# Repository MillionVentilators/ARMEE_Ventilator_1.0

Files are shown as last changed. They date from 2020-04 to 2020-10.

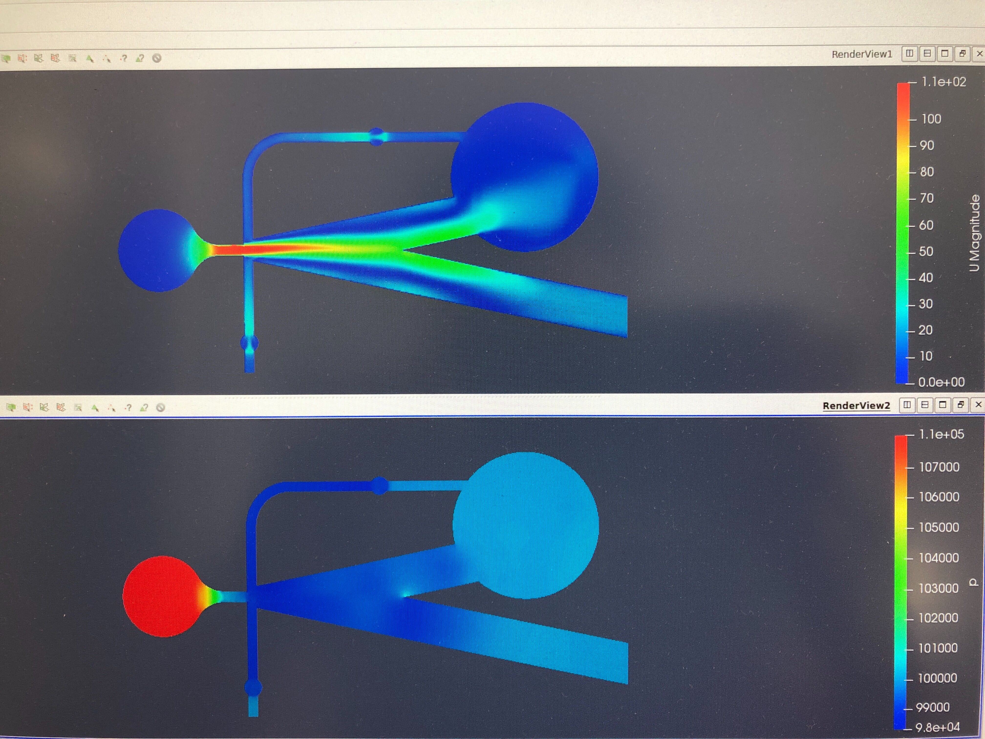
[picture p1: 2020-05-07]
experimental/Monostable/images/Image from iOS (16).jpg

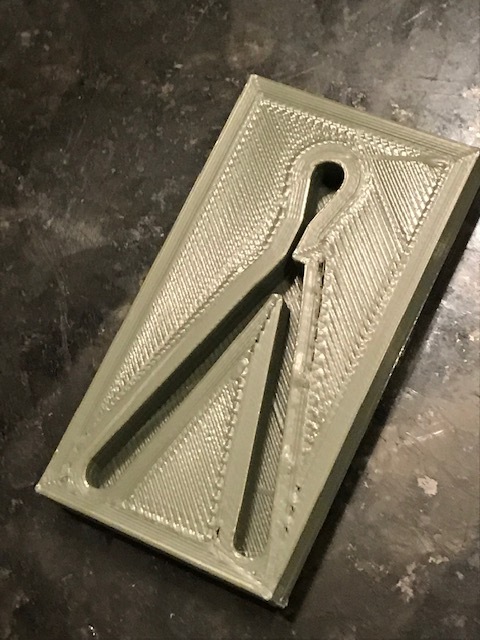
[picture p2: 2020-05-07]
experimental/Monostable/images/IMG_2069.jpg

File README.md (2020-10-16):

# ARMEE Ventilator

Automatic Respiration Management Exclusively for Emergencies

www.ARMEEVentilator.com (previously www.ARMEEVent.com)

Email: ArmyVent@gmail.com

Introduction: (click for video)
ARMEE Ventilator Introduction (https://www.youtube.com/watch?v=14Afl-Eg2tM "ARMEE Ventilator Introduction")

## INTRO

This repository contains plans for a device which controls air (or gas) flow so that its output alternates between two pressure levels.  The pressures, flow rates and cycle times are similar to the typical output of a mechanical ventilator.  *It has no moving parts*, and could be produced very rapidly, at low cost and in very large numbers if needed.

The original design dates to the early 1960s:
* J.W. Joyce, Jr. ["TM 68-30 The Army Emergency Respirator"](./research/1968_Army_Emergency_Respirator.pdf). Harry Diamond Labs, US Army Materiel Command, 1968

We are working to modify it to make the output better match modern requirements.

This is an open source hardware project: all work is licensed under the CERN Open Hardware Licence v2 (strongly reciprocal).

## HOW TO CONTRIBUTE

Get the necessary [Equipment](./documentation/Equipment.md): a source of compressed air, pressure and flow gauges and a test lung.

Build one of the [Stable Models](./stable/), following the [Build Instructions](./documentation/Build_Instructions.md): the recommended method is to use a CNC mill to make this out of plastic, but feel free to experiment.

The [Monostable](./experimental/Monostable) design is currently the most promising model, with results close to target parameters and very stable switching.  Check it out.

Run some tests following the [Test Instructions](./documentation/Test_Instructions.md).

Try to modify the design so as to address some of the [Open Issues](./documentation/Open_Issues.md).

Participate in the discussion on [Helpful Engineering](http://helpfulengineering.slack.com) at #project-oscillating-ventilator or our [Slack](http://millionvents.slack.com).

## MORE DOCUMENTATION

(Now somewhat outdated) documentation: 
- https://docs.google.com/document/d/1ZnPGnA-GKtFLsJEDVVLLKqNAKSk3q6F47YqvtuoJVXw/

## DISCLAIMER

This is not a medical device, and is not intended to be used as part of a medical device. It is especially not intended to be used in critical life support equipment. It comes with ABSOLUTELY NO WARRANTY. If you build it and use it, you do so at your own risk. If you build devices incorporating this design and use them for any application, it is up to you to verify the performance is suitable for your application and complies with all applicable laws.

## COPYRIGHT AND LICENSE

Copyright 2020 
- Ryan Whitney M.ryan.whitney@gmail.com (PEEP Loop Models)
- Alex Izvorski aizvorski@gmail.com (Original Dimensions/Models)
- Chris Jung Chris@braeburnacoustics.com (CNC Machining Models)
- Arrtemio Mendoza artexmg@gmail.com (3D Printing Models)

This Source (CAD files and other design materials) describes Open Hardware and is licensed under the CERN-OHL-S v2.

You may redistribute and modify this Source and make products using it under the terms of the CERN-OHL-S v2 (https:/cern.ch/cern-ohl).

This documentation is distributed WITHOUT ANY EXPRESS OR IMPLIED WARRANTY, INCLUDING OF MERCHANTABILITY, SATISFACTORY QUALITY AND FITNESS FOR A PARTICULAR PURPOSE. Please see the CERN-OHL-S v2 for applicable conditions.

Source Location: https://github.com/MillionVentilators/ARMEE_Ventilator_1.0

As per CERN-OHL-S v2 section 4, should You produce hardware based on this Source, You must maintain the Source Location visible on the external case of the hardware or other product you make using this Source.

## DISCLAIMER OF WARRANTY, EXCLUSION AND LIMITATION OF LIABILITY

Additionally, the following important disclaimers from the CERN-OHL-S v2 license apply to all use (reproduced below for clarity). Do not download or use these files unless you have read and agree with the following.

6.1 DISCLAIMER OF WARRANTY -- The Covered Source and any Products are provided 'as is' and any express or implied warranties, including, but not limited to, implied warranties of merchantability, of satisfactory quality, non-infringement of third party rights, and fitness for a particular purpose or use are disclaimed in respect of any Source or Product to the maximum extent permitted by law. The Licensor makes no representation that any Source or Product does not or will not infringe any patent, copyright, trade secret or other proprietary right. The entire risk as to the use, quality, and performance of any Source or Product shall be with You and not the Licensor. This disclaimer of warranty is an essential part of this Licence and a condition for the grant of any rights granted under this Licence.

6.2 EXCLUSION AND LIMITATION OF LIABILITY -- The Licensor shall, to the maximum extent permitted by law, have no liability for direct, indirect, special, incidental, consequential, exemplary, punitive or other damages of any character including, without limitation, procurement of substitute goods or services, loss of use, data or profits, or business interruption, however caused and on any theory of contract, warranty, tort (including negligence), product liability or otherwise, arising in any way in relation to the Covered Source, modified Covered Source and/or the Making or Conveyance of a Product, even if advised of the possibility of such damages, and You shall hold the Licensor(s) free and harmless from any liability, costs, damages, fees and expenses, including claims by third parties, in relation to such use.

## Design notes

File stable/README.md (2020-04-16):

# Models

## Harry_Diamond_Respirator

(step and f3d files)

A replica of the original 1960s vintage US Army device.

Modeler: Alex Izvorski

Dimensions were obtained from a physical museum piece found in an art gallery in Chicago which is one of the only known copies in existence (so far) of the original 1968 US ["Army Emergency Respirator"](./research/1968_Army_Emergency_Respirator.pdf) developed at Harry Diamond Labs.

If constructed carefully, this is expected perform identically to the original, cycling at a useful range of pressures/rates depending on input flow and calibration; and also including having a negative end pressure (which is not a desirable property).  

Note: we have had problems with reproducibility, probably because of small air leaks between the two halves of the device.  Dimensions and surface finish are also very important, probably +-0.02mm and ISO N6 finish or better.

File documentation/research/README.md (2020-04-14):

# References

Repository to host non-copyrighted patents and research materials found through our development process, as well as link references to online copyrighted versions.

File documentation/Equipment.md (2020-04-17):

# Equipment

## Compressed air

A source of pressurized air capable of 100 lpm (2 cfm) at 340 kPa (50 psi)

Suggested: small oil-free air compressor, eg Porter Cable C2002

Set the output of the compressor to a regulated 50psi, and connect a precision flow adjustment valve: McMaster-Carr 46425K12 or equivalent.

## Medical gas flow analyzer or ventilator tester

Device intended for certifying performance of ventilators in hospitals; contains pressure, flow and gas composition sensors.

Suggested 1: Fluke VT Plus HF; Fluke VT650 or VT900; TSI Certifier 4080; IMT Citrex H3, H4, H5.
These are expensive, typically > $2000 used.

Suggested 2: Siargo FS6122 or certain Sensirion  / Honeywell sensors have the right specs, but are not easy to interface

If gas flow analyzer is unavailable, a pressure gauge and flow gauge may be used as a substitute in a pinch.

## Pressure gauge

Pressure gauge capable of measuring 0-50 cmH2O with <1 cmH2O accuracy

Suggested 1: HT Instrument HT 805 Bluetooth Digital Manometer

Suggested 2: U tube manometer made out of 50-80 cm long piece of clear tubing with 1/4" or 1/8" inner diameter (eg aquarium PVC tubing)

Note: these pressures are far too low for most pressure gauges, other than the gauges used for HVAC service.

## Flow gauge

Flow gauge capable of measuring +-50 lpm air flow with <1 lpm accuracy.  (+-100lpm and <0.1 lpm accuracy is preferred) 

Suggested 1: medical flow meter (combination rotameter and needle valve) eg Timeter, Amvex, Ohmeda brand - this is not ideal, but don't really have a recommendation for a good digital sensor yet.  Most of these only span 0-15 lpm; may need more than one to cover 0-15 and 0-50 ranges.

Suggested 2: use a known resistance (~5mm hole in much larger tube) and differential pressure gauge from above to convert pressure drop to flow - also not ideal, have to always do math to convert, flow is proportional to square root of pressure drop.

## Test lung

A lung simulator with known (and preferably adjustable) resistance and compliance, within the range of C20-C50 ml/cmH2O and R5-R20 cmH2O/(liter/second).

Suggested: rigid vessel 30-70 liters (7.5-19 gallons) in size, with an entry opening restricted to 5-8mm in diameter.  Follow directions in this article [How To Make Your Own Accurate Test Lungs](https://medium.com/@RobertLeeRead/how-to-make-your-own-accurate-test-lungs-for-testing-emergency-ventilators-2d68fe5ac460)

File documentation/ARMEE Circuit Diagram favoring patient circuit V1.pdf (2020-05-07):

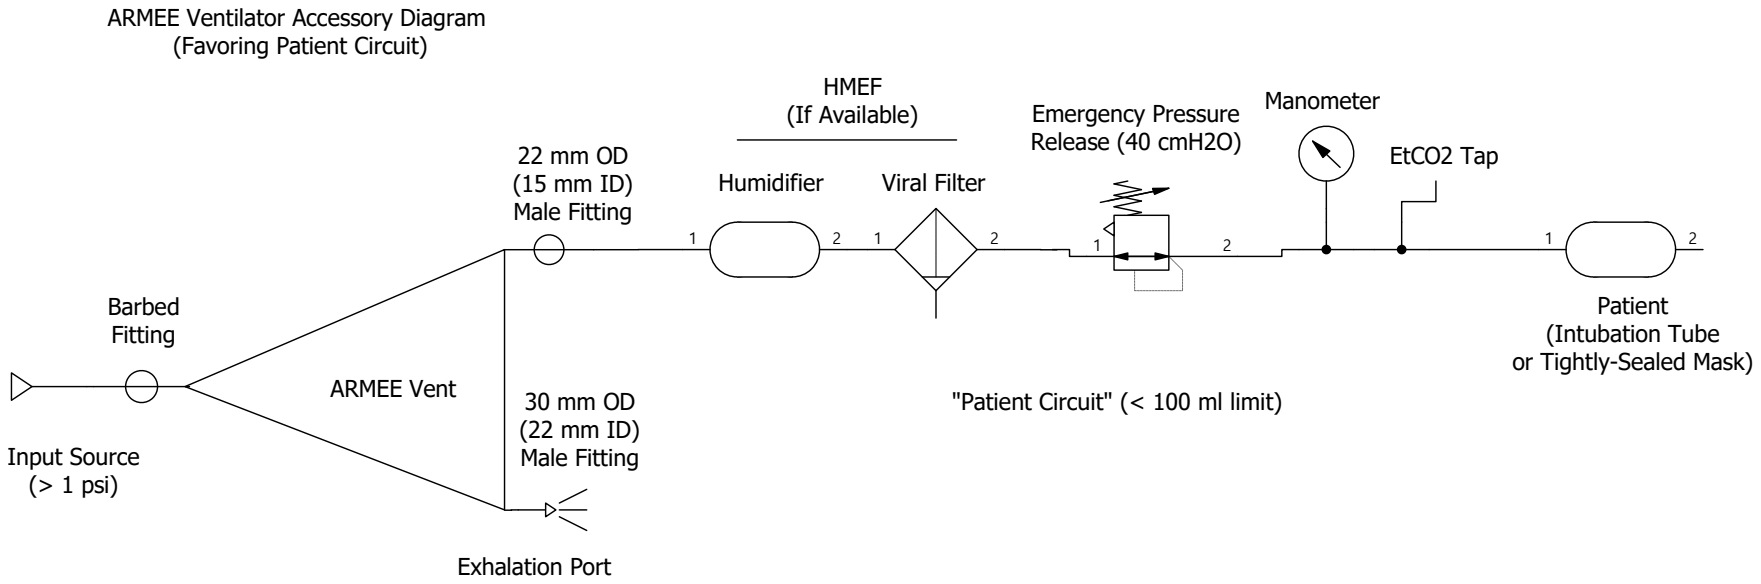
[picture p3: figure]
EtCO2 Tap; Manometer; Patient (Intubation Tube or Tightly-Sealed Mask); Emergency Pressure Release (40 cmH2O); Input Source (> 1 psi); ARMEE Ventilator Accessory Diagram (Favoring Patient Circuit); Viral Filter; HMEF (If Available); Exhalation Port; 22 mm OD (15 mm ID) Male Fitting; Barbed Fitting; Humidifier; 30 mm OD (22 mm ID) Male Fitting

"Patient Circuit" (< 100 ml limit) ARMEE Vent

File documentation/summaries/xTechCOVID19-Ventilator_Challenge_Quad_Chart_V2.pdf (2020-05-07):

## Interstate Disaster Medical Cooperative

## Automatic Respiration Management Exclusively for Emergencies

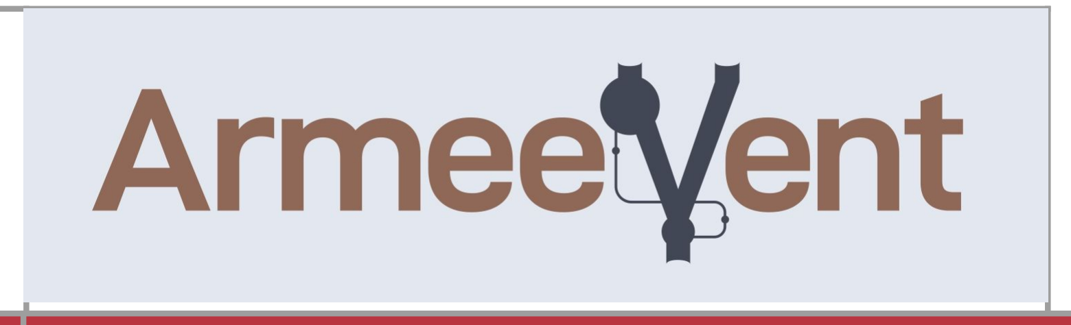
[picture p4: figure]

Tech. & Team | Mission Alignment | Technical Viability

Resubmission:

ARMEE Vent
Inspired by 1960s
designs and modified for
positive PEEP

Device Diagram:

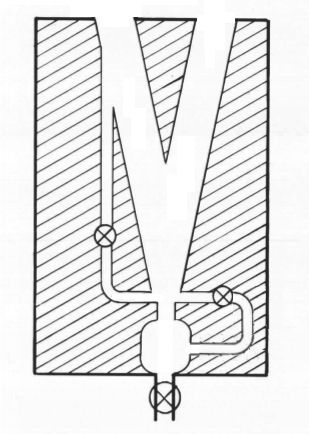
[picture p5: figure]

Core Team:
EMS Medical Director,
Medical Device Engineer,
Manufacturing Expert,
CFD Scientist,
Project Manager

Device is rugged, solid-state, has no moving parts, and is roughly the size/weight of a deck of cards - making it suitable for any kit. It is pneumatic (air-powered) and runs on low-pressure air or O2. This is a Pressure-Controlled device which also allows patient-triggered breathing, suitable for invasive or non-invasive ventilation. It can be customized to target any of the following: positive PEEP (5-20), PIP (15-35), I:E ratio (1:1 to 1:3), RR (0-60), TV (50-1000), for large or small patients with healthy lungs or damaged ones. The device is modular, fitting standard hospital tubing, and can operate standalone or with a suite of alarms/sensors/emergency valves, optionally included.

We use well-researched fluid dynamics science (fluid amplifiers) to build a suite of devices with pressure profiles built-in to the geometry of the devices to offer a range of PIP/PEEP/I:E ratio combos which can be targeted for different patient sizes and lung-health levels. While an unusual way to solve the problem, patients infrequently have their prescriptions changed in an emergency/pandemic situation, so simply swapping device models to match at those times is sufficient - and we offer the ability for more fine-grained adjustments via changing Input Flow as well. Multiple doctors endorse this approach already, and will be given rigorous data charts to guide applicability of the device.

Regulatory | Speed

Originally based on 1965 US Army ventilator research,
which was tested on dogs and humans successfully, we
have modified the designs and are underway with our own clinical testing. The design is very simple, easily cleaned or disposed-of, and runs indefinitely given a consistent flow of air. It can be easily swapped for a BVM, or fitted with (optional) additional safety precautions which give it full alarm and sensor functionality. Aside from an input flow rate of 20-30 lpm (which version 2 will fix), the device meets the UK's RMVS ventilator standards, and we expect it to pass EUA regulations once the final product is packaged.

A single CNC machine could immediately begin producing hundreds of units per day at sub-$30 ppu. Injection Molding: thousands per day, sub-$5. 3D printing: around 10 per day, sub-$5 ppu - useful for forward-deployment or on-demand production. Overall: 10k could be made in one day with 20-30 CNC machines with no lead-in time. That said, we recommend a sub-5-minute quality test per device, and we warn that the optional alarms/sensors may not match production speed. These are easier to source or create out of existing materials though, and may not be needed for every patient. We have several interested manufacturing partners.

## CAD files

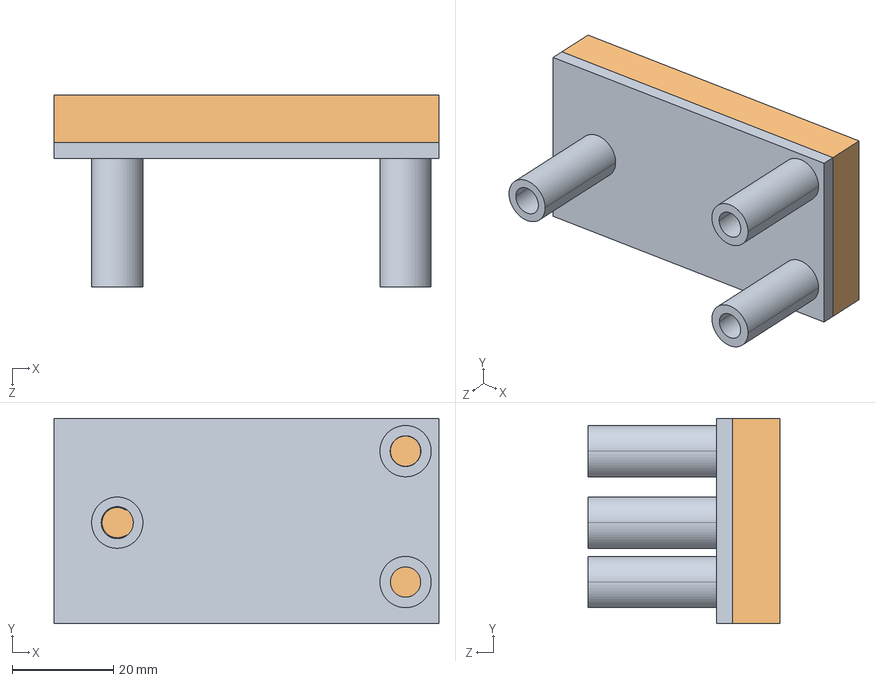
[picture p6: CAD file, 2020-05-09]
experimental/Monostable/Assembly_Monostable Fluidic Amplifier_Alpha Design_Nozzle_1.3mm__Radius_63.5mm__Channel Depth_6mm__Fillet_0mm.STEP
76.2 x 40.6 x 38.0 mm

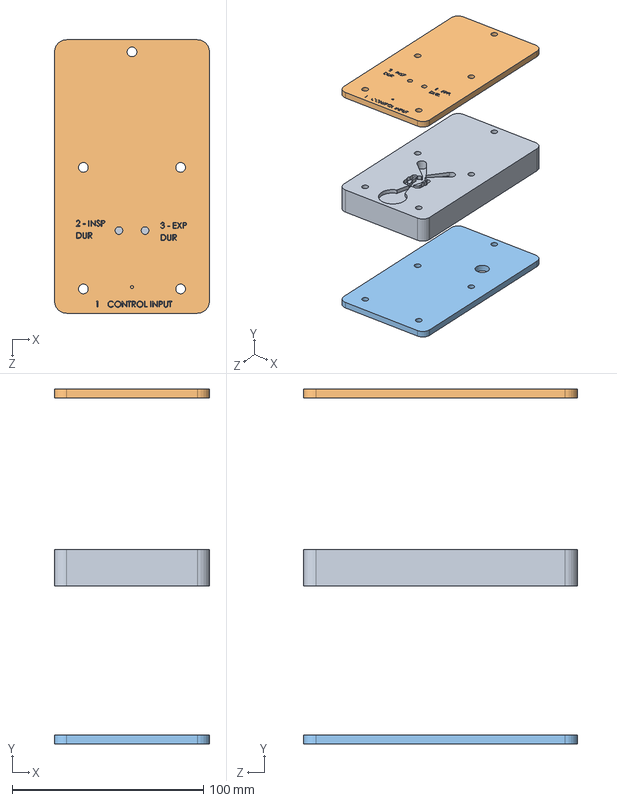
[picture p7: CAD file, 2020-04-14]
experimental/misc/Volume_Control/models/v2_whitney/NASA Army Vent Assm 02.SLDASM
81.0 x 185.4 x 142.9 mm
NASA Army Vent Body 02
Nasa Vent Plate 02, Control Side
Nasa Vent Plate 02, Flow Side

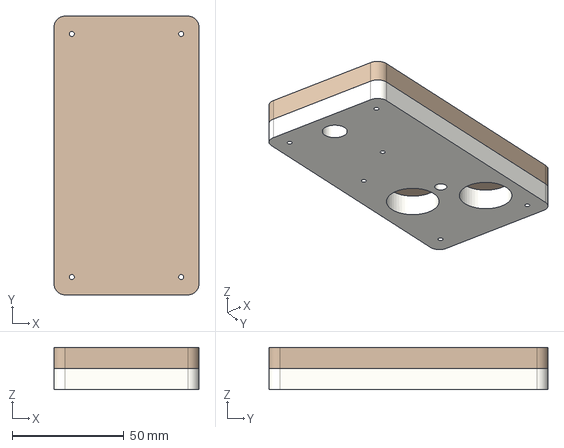
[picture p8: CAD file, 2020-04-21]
experimental/Exhaust_PEEP/Exhaust_PEEP v7.step
65.0 x 125.0 x 19.1 mm

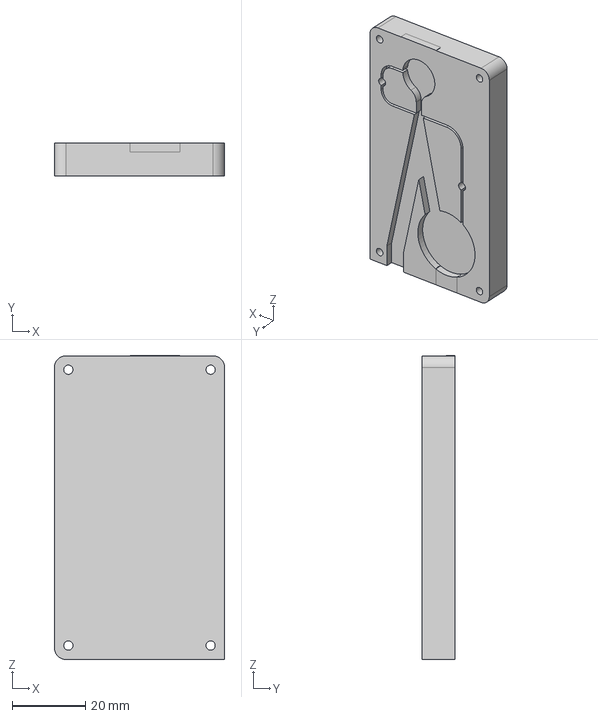
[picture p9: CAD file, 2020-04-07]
experimental/Loop_PEEP/models/CNC_machining/ARMEE_1.0_machinable.step
46.5 x 8.89 x 83.1 mm

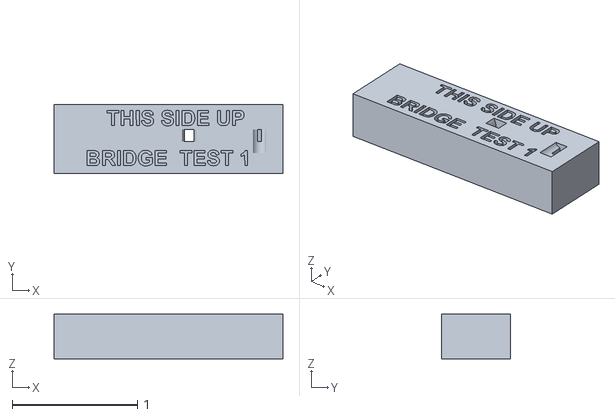
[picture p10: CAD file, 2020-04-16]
experimental/Loop_PEEP/models/FDM_3D_Printed_Brick/Bridge Test 1.stl
1.83 x 0.55 x 0.356

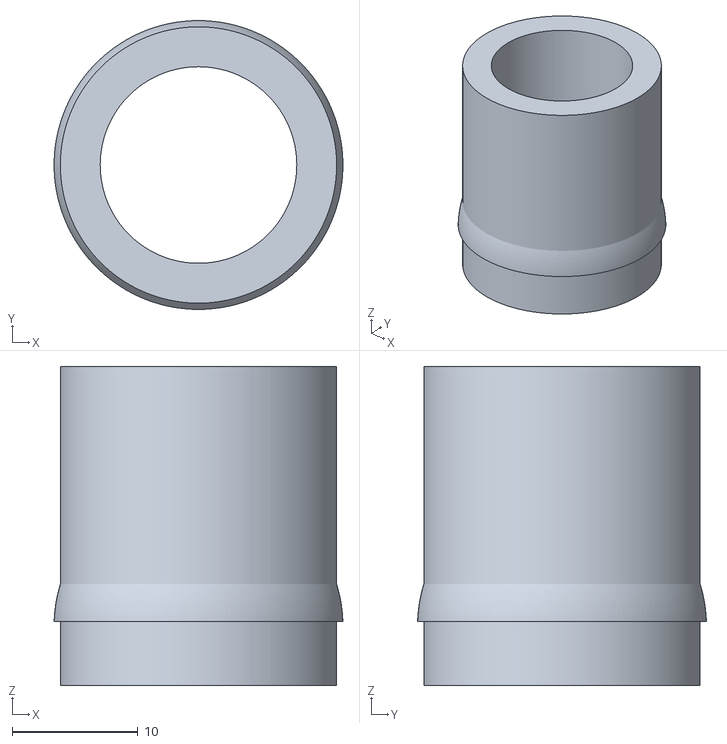
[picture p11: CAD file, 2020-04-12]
experimental/Loop_PEEP/models/FDM_3D_Printed_Snap/Outlet Armee1.stl
23.0 x 23.0 x 25.4

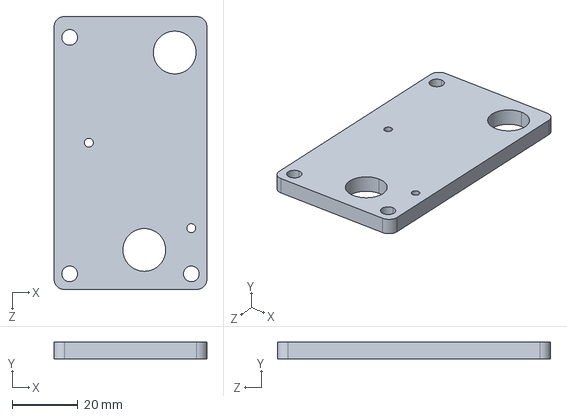
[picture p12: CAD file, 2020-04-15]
experimental/Loop_PEEP/models/HPDC_estimates/Army Vent PEEP 02, Lid_HPDC_r0.STEP
46.5 x 5.16 x 83.0 mm

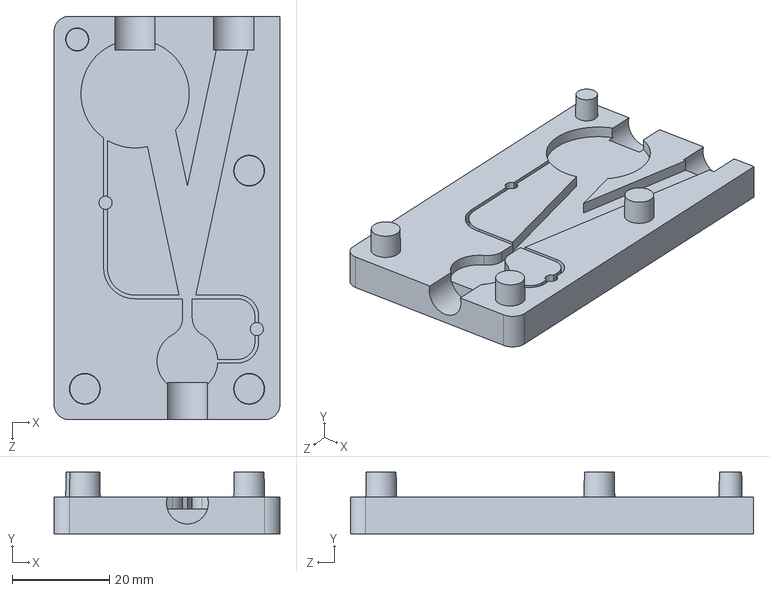
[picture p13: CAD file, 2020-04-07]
experimental/Loop_PEEP/models/reference_design/v2_whitney/ARMEE_1.0_base.sldprt
46.5 x 12.7 x 83.0 mm

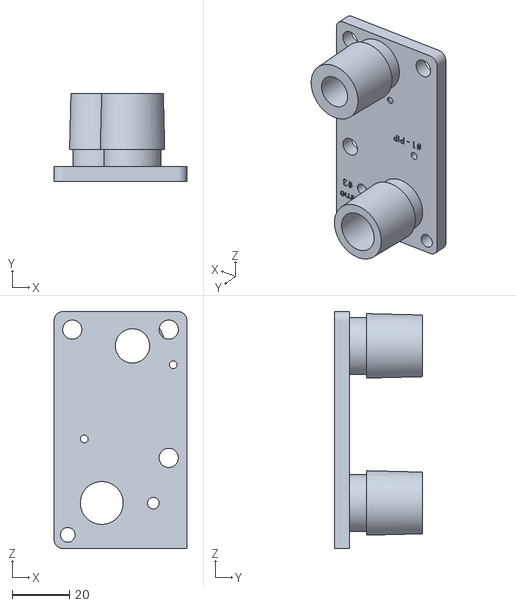
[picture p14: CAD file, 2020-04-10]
experimental/Loop_PEEP/models/reference_design/v3_whitney/Army Vent PEEP 03, Lid_20200410.STL
46.5 x 30.7 x 83.0

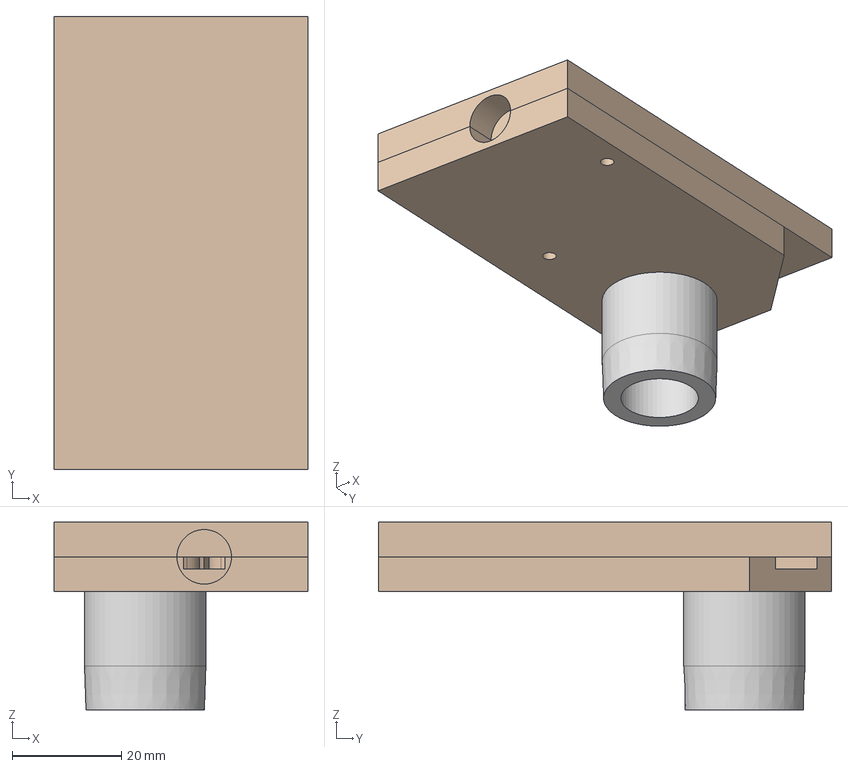
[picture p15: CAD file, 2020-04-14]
experimental/Loop_PEEP/models/reference_design/v4_whitney/Harry_Diamond_PEEP_Ryan v4.step
46.5 x 83.0 x 34.4 mm

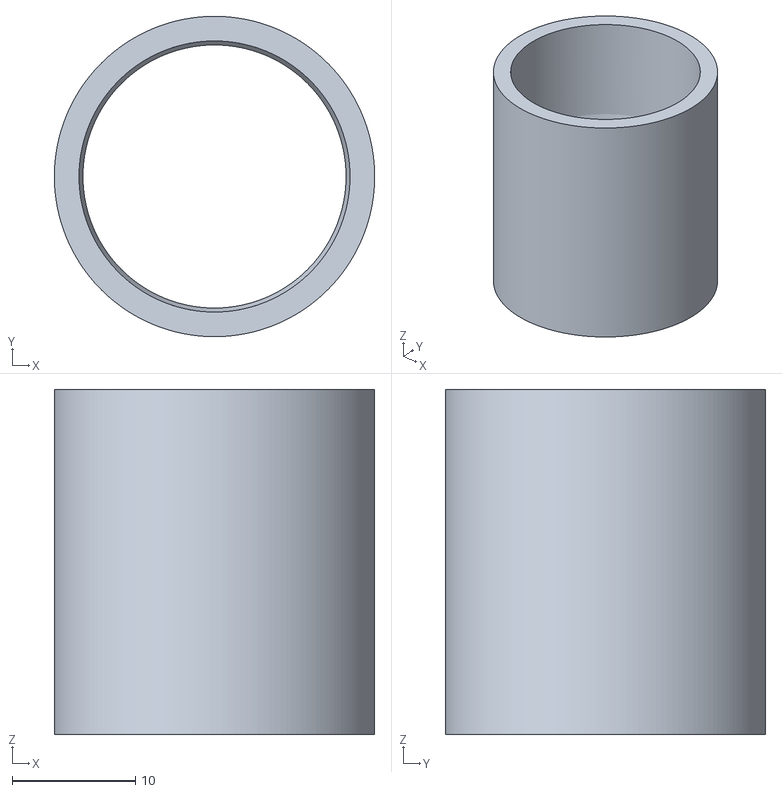
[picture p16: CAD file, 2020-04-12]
experimental/misc/Fittings/Couple 22mm Male.stl
26.0 x 26.0 x 28.0

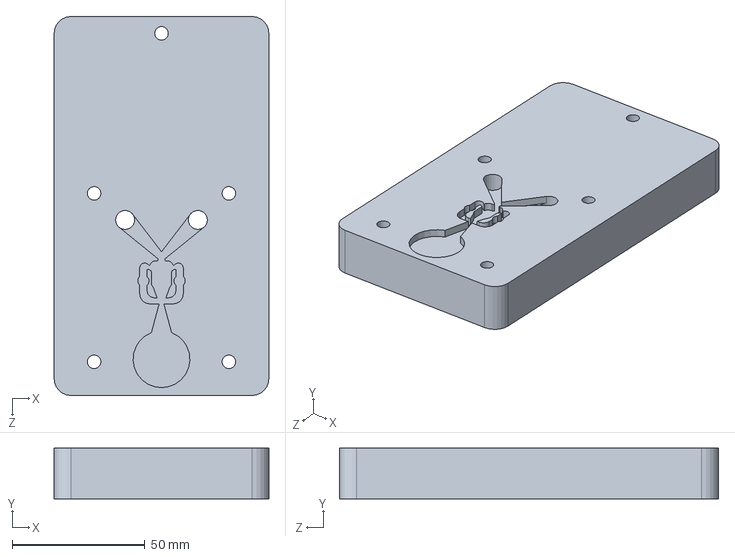
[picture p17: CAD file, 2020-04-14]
experimental/misc/Volume_Control/models/v2_whitney/NASA Army Vent Body 02.SLDPRT
81.0 x 19.1 x 142.9 mm

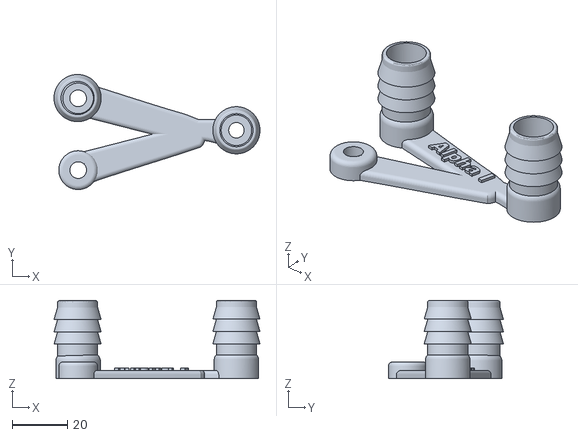
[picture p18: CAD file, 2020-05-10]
experimental/Monostable/Highly Printable - Alpha I/FDM/Two Parts/Alpha I Rev1 - Top.stl
74.3 x 41.5 x 28.2

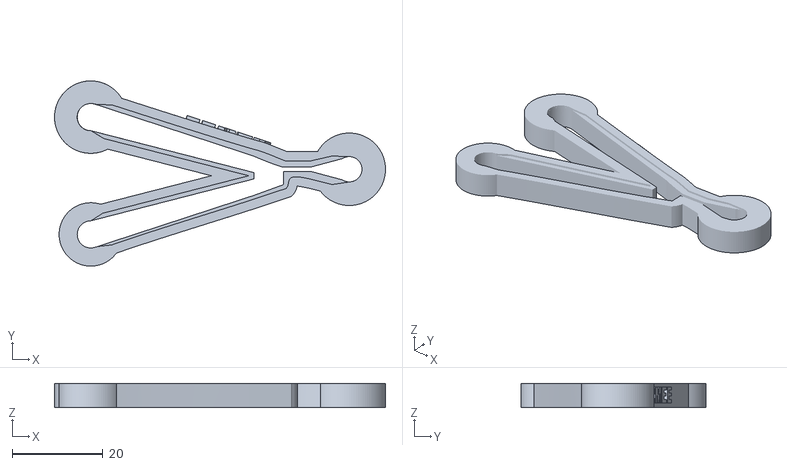
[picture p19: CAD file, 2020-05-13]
experimental/Monostable/Highly Printable - Alpha I/FDM/Unibody/Alpha I Rev1 - Testing Gasket.stl
73.1 x 40.9 x 5.31

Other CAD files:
experimental/Harry_Diamond_DFM/Harry_Diamond_DFM v4.step
experimental/Loop_PEEP/models/reference_design/v5_whitney/Harry_Diamond_PEEP_Ryan v5.step
experimental/Loop_PEEP_3Way/Loop_PEEP_3Way v3.step
experimental/Monostable/Highly Printable - Alpha I/SLA/Alpha I Rev1 - Unibody SLA.stl
experimental/Exhaust_PEEP/Exhaust_PEEP v7.f3d
experimental/Harry_Diamond_DFM/Harry_Diamond_DFM v4.f3d
experimental/Loop_PEEP/models/CNC_machining/ARMEE_1.0_machinable.f3d
experimental/Loop_PEEP/models/CNC_machining/ARMEE_1.0_test_rig.f3d
experimental/Loop_PEEP/models/CNC_machining/ARMEE_1.0_test_rig.step
experimental/Loop_PEEP/models/FDM_3D_Printed_Brick/ARMEE_1.0_printable_brick_fat_feedback.stl
experimental/Loop_PEEP/models/FDM_3D_Printed_Brick/Armee1 - Unibody Brick V1.1.stl
experimental/Loop_PEEP/models/FDM_3D_Printed_Brick/ArmyVentPEEP02 BRICK REV AMG.stl
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

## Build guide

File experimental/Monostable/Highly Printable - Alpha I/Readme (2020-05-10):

READ THIS BEFORE ANYTHING, you will need it!
Prepared by Artemio Mendoza

Before we start, let me say that THIS VENTILATOR IS NOT A MEDICAL EQUIPMENT, it is NOT INTENTED TO BE USED IN HUMAN PATIENTS.

This is a single piece ventilator (unibody). It is highly printable using either FDM or SLA 3D printers.

SLA.

For SLA it is as simple as printing in one single piece. Nothing much to add here, just get the STL from SLA directory and print it.
Of course you need to orient the print to avoid suction due to cups formation by the internal channels of the print. 
But you already know that, after all you have a SLA printer! :-) 

FDM.

1- Unibody version:

In order to print a single body ventilator using a FDM I developed a technique I call assisted bridging (or eZ-bridging or patching). 
It consists in pre-printing a flat support to be placed manually latter in the print to scaffold the next layer. 
Such a layer will become the ceiling of the print.

In order to place the printed support (or patch) you will need to stop the print, place the patch manually and then 
continue printing from where it stopped. This can be achieved modifying the Gcode either manually or by script 
in your slicing software. You would find the document "eZ-bridging.doc" usefull to get more details on this technique.

It is simpler than you think and once you get the hang of it, you will be able to bridge other pieces you always wanted to print, 
but you cannot because your printer did not like bridging. Now she will like bridging.

2.- Two parts version:

If for some reason you want to print the ventilator in two parts, you can find this two pieces in the directory "Two Parts". 
You can print both pieces and then glue them together. 

Final words: THIS VENTILATOR IS NOT A MEDICAL EQUIPMENT, it is NOT INTENTED TO BE USED IN HUMAN PATIENTS!

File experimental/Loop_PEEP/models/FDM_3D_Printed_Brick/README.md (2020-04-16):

# 3D-Printed "Brick" Version

by Artemio Mendoza

A single-print "brick" version made for FDM 3D Printers

1) Look the picture "how to orient the piece for printing"

2) Print the test pieces to validate your printer capabilities

Good luck!

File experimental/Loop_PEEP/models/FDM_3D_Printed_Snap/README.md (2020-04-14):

# 3D-Printed "Snap" Version

by Artemio Mendoza

A single-print "snap" version made for FDM 3D Printers, with printable fittings which snap-in to the device.

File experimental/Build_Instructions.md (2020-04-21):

# Build instructions

These instructions are common for the models in Harry_Diamond_DFM, Loop_PEEP_3Way and Exhaust_PEEP.

## CNC

The device is constructed from 3/8" polycarbonate sheet stock, McMaster-Carr 8574K31 or equivalent.  It may be possible to use 1/4" inch sheet stock, McMaster-Carr 8574K172, however in that case the NPT fittings should be carefully screwed in to a depth of no more than 4mm so they don't block the channels. For prototyping, acrylic may be used instead of polycarbonate; it is more fragile, and does not resist alcohol-based cleaning agents.

Drill and tap the holes in the base.  The large output and vent holes are 3/4 NPT.  The input and side vent are 1/4 NPT.  The adjustment screws are 4-40, except for one larger screw which is 1/4-28.

Mill the channels into the top piece to the depth and width shown in the CAD file +- 0.05mm, using a CNC mill.  Channel cross section area is a critical dimension.  Do NOT mill the face which will become a joint between the pieces: it should have the original smooth surface from the plastic sheet.  Make sure the channel sides and bottom are smooth (surface finish ISO N6 or better).

Make sure that there are no burrs left, and the face which will be joined to the other piece is flat.

Clean and degrease the mating surfaces thoroughly.

Spread a thin, uniform layer of water-thin acrylic solvent cement: IPS Weld-On 3, SciGrip 3, McMaster-Carr 7528A13 or equivalent, on the entire cover piece, then press the base piece onto it with the channels pointed DOWN (so that the solvent doesn't drip into the channels).  Clamp with 200 lb force.  Let sit for 30 minutes while keeping the channels pointed down the whole time.  Do this step in a fume hood as the solvent cement is toxic if inhaled.  Full joint strength requires >24 hours.

Inspect the weld.  The weld should be essentially invisible; there may be a few bubbles, and a bit of squeeze-out at the edges of the channels, but there should be no large voids allowing leakage between channels, and no voids near the power nozzle/main jet.

Adjustment screws:  
- Stainless Steel Flat-Tip Set Screws, 4-40, 1/4" long, McMaster-Carr 94355A140
- Stainless Steel Flat-Tip Set Screws, 1/4-28, 1/4" long, McMaster-Carr 94355A602

Output fittings:    
- Plastic Barbed Tube Fitting, 3/4 NPT x 3/4 barb, nylon, McMaster-Carr 5372K133 or 53415K217	

These can be connected to 22mm tapered fittings common in respiratory care with short pieces of 3/4 silicone tubing, McMaster-Carr 5236K527.

Input and side vent: 
- Plastic Barbed Tube Fitting, 1/4 NPT x 1/4 barb, nylon, McMaster-Carr 5372K112 or 5121K451
(side vent may be optionally connected to 1/4 NPT x 3/4 barb, McMaster-Carr 5372K122)

Note: NPT fittings are typically seated to a depth of 4mm (finger tight) to 7mm (maximum, requires wrench).  Make sure they are not seated deep enough to block the channels; if using 1/4 sheet stock, the maximum depth is 4mm.

Note: these fittings are ONLY suitable for testing; medical connectors tend to use completely different types of connections.

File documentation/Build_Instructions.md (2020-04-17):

# Build instructions

## CNC

The device is constructed from 1/4" polycarbonate sheet stock, McMaster-Carr 8574K172 or equivalent.
(Note: some models use 3/8" or 1/2" inch sheet stock; acrylic may be used instead of polycarbonate)

Mill the channels into the top piece to the depth and width shown in the CAD file +- 0.05mm, using a CNC mill.  Channel cross section area is a critical dimension.  Do NOT mill the face which will become a joint between the pieces: it should have the original smooth surface from the plastic sheet.  Make sure the channel sides and bottom are smooth (surface finish ISO N6 or better).

Tap the adjustment screw holes using a M3x0.5 tap.  Make sure that there are no burrs left, and the face which will be joined to the other piece is flat.

Clean and degrease the mating surfaces thoroughly.

Spread a thin, uniform layer of water-thin acrylic solvent cement: IPS Weld-On 3, SciGrip 3, McMaster-Carr 7528A13 or equivalent, on the bottom piece, then press the top piece onto it.  Clamp and let sit for 30 minutes; full joint strength requires >24 hours.  Do this step in a fume hood as the solvent cement is toxic if inhaled.

Tap the input fitting hole using a M6x1 tap.  Clamp the piece to prevent the joint cracking during the tapping operation.

Adjustment screws: Stainless Steel Flat-Tip Set Screw, M3 x 0.5 mm Thread, 6 mm Long 
McMaster-Carr 92605A100 

Input fitting: Stainless Steel Barbed Tube Fitting, 4mm Tube ID, M6 x 1 mm Male
McMaster-Carr 4406T772

## 3D printing

The same geometry can be printed using SLA for prototyping (eg on a Form 3 printer).  SLS and MJF *may* work but the tolerances are about 5x what is needed, and the surface roughness is much greater as well.  FDM is probably not suitable due to the tolerances needed.

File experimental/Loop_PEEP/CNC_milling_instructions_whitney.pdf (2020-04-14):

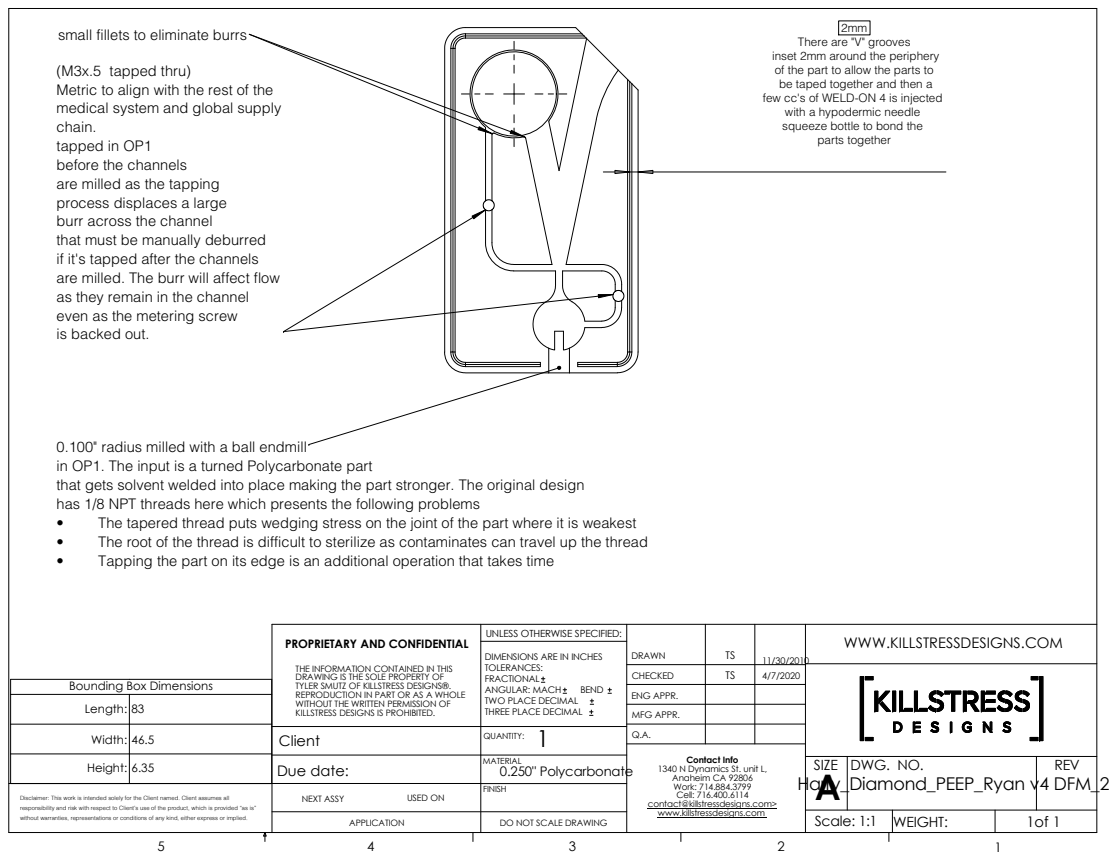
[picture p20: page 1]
Harry_Diamond_PEEP_Ryan v4 DFM_2; BEND; small fillets to eliminate burrs; 2mm There are "V" grooves; parts together

inset 2mm around the periphery
of the part to allow the parts to
be taped together and then a
few cc's of WELD-ON 4 is injected
with a hypodermic needle
squeeze bottle to bond the

(M3x.5 tapped thru)
Metric to align with the rest of the
medical system and global supply
chain.
tapped in OP1
before the channels
are milled as the tapping
process displaces a large
burr across the channel
that must be manually deburred
if it's tapped after the channels
are milled. The burr will affect flow
as they remain in the channel
even as the metering screw
is backed out.

0.100" radius milled with a ball endmill
in OP1. The input is a turned Polycarbonate part
that gets solvent welded into place making the part stronger. The original design
has 1/8 NPT threads here which presents the following problems
• The tapered thread puts wedging stress on the joint of the part where it is weakest
• The root of the thread is difficult to sterilize as contaminates can travel up the thread

Tapping the part on its edge is an additional operation that takes time

PROPRIETARY AND CONFIDENTIAL THE INFORMATION CONTAINED IN THIS DRAWING IS THE SOLE PROPERTY OF TYLER SMUTZ OF KILLSTRESS DESIGNS®. REPRODUCTION IN PART OR AS A WHOLE WITHOUT THE WRITTEN PERMISSION OF KILLSTRESS DESIGNS IS PROHIBITED. | UNLESS OTHERWISE SPECIFIED: | DRAWN | TS | 11/30/2010 | WWW.KILLSTRESSDESIGNS.COM

DIMENSIONS ARE IN INCHES
TOLERANCES:
FRACTIONAL
ANGULAR: MACH
TWO PLACE DECIMAL
THREE PLACE DECIMAL

CHECKED | TS | 4/7/2020
ENG APPR.
MFG APPR.

Bounding Box Dimensions

Length: 83

Width: 46.5 | | Client | 1 QUANTITY: | Q.A.
Height: 6.35 | | Due date: | MATERIAL 0.250" Polycarbonate | | SIZE A | DWG. NO. | REV

Contact Info
1340 N Dynamics St. unit L,
Anaheim CA 92806
Work: 714.884.3799
Cell: 716.400.6114
contact@killstressdesigns.com>
www.killstressdesigns.com

Disclaimer: This work is intended solely for the Client named. Client assumes all responsibility and risk with respect to Client’s use of the product, which is provided “as is” without warranties, representations or conditions of any kind, either express or implied. | | NEXT ASSY USED ON | FINISH

APPLICATION | DO NOT SCALE DRAWING | | Scale: 1:1 | WEIGHT:

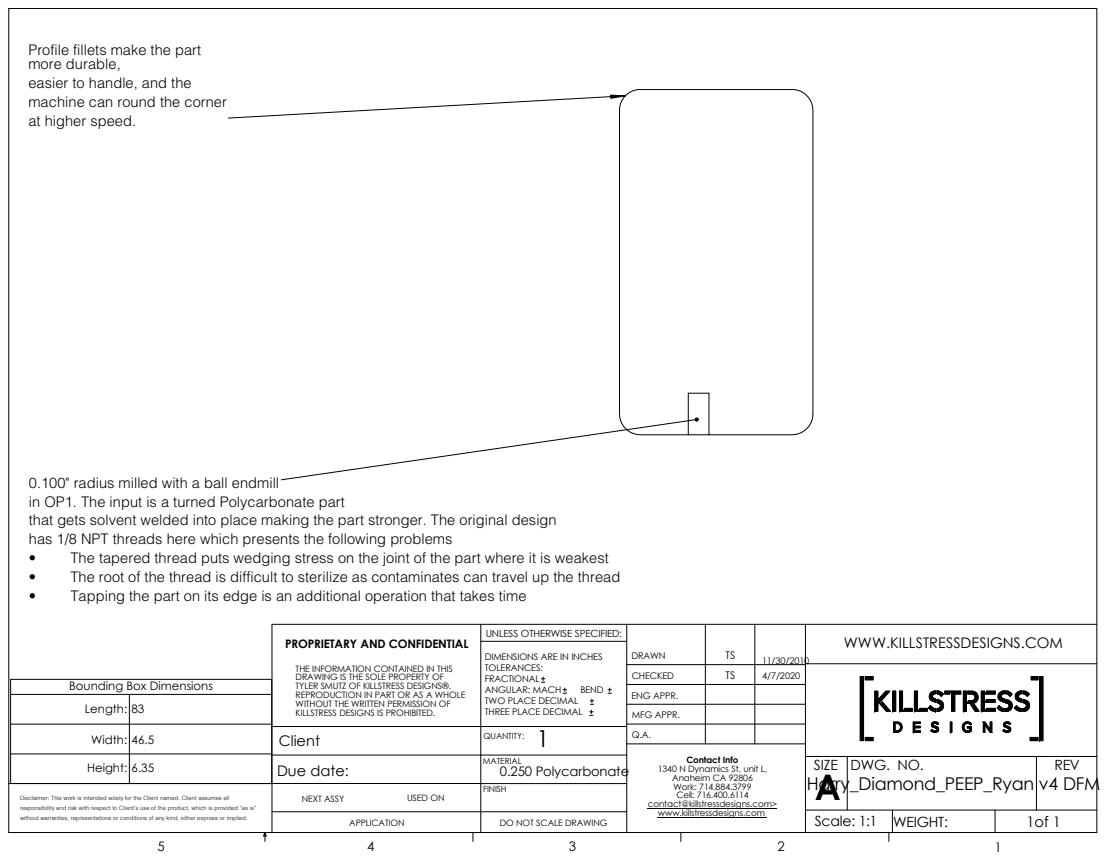
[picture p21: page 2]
DRAWN; DWG. NO.; REV; REPRODUCTION IN PART OR AS A WHOLE; TWO PLACE DECIMAL; 0.250 Polycarbonate; MATERIAL; Contact Info; Due date:; SIZE; UNLESS OTHERWISE SPECIFIED:; WWW.KILLSTRESSDESIGNS.COM; BEND; Harry_Diamond_PEEP_Ryan v4 DFM; Height: 6.35

Profile fillets make the part
more durable,
easier to handle, and the
machine can round the corner
at higher speed.

0.100" radius milled with a ball endmill
in OP1. The input is a turned Polycarbonate part
that gets solvent welded into place making the part stronger. The original design
has 1/8 NPT threads here which presents the following problems
• The tapered thread puts wedging stress on the joint of the part where it is weakest
• The root of the thread is difficult to sterilize as contaminates can travel up the thread
• Tapping the part on its edge is an additional operation that takes time

PROPRIETARY AND CONFIDENTIAL

THE INFORMATION CONTAINED IN THIS
DRAWING IS THE SOLE PROPERTY OF
TYLER SMUTZ OF KILLSTRESS DESIGNS®.
WITHOUT THE WRITTEN PERMISSION OF
KILLSTRESS DESIGNS IS PROHIBITED.

DIMENSIONS ARE IN INCHES
TOLERANCES:
FRACTIONAL
ANGULAR: MACH

CHECKED | TS | 4/7/2020
ENG APPR.
MFG APPR.

Bounding Box Dimensions

Length: 83
Width: 46.5 | | Client | 1 QUANTITY: | Q.A.

THREE PLACE DECIMAL

1340 N Dynamics St. unit L,
Anaheim CA 92806
Work: 714.884.3799
Cell: 716.400.6114

without warranties, representations or conditions of any kind, either express or implied. | NEXT ASSY USED ON | FINISH

DO NOT SCALE DRAWING | | Scale: 1:1

0

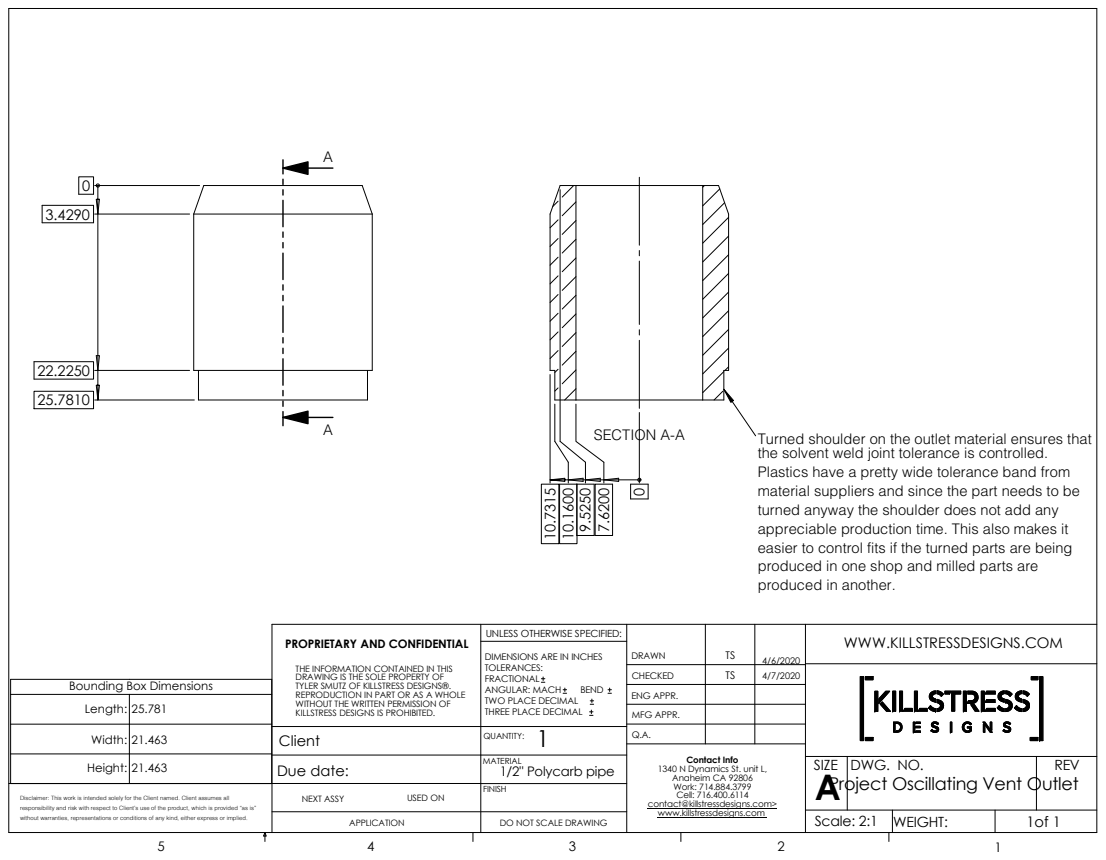
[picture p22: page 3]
Work: 714.884.3799; Due date:; 1340 N Dynamics St. unit L,; CHECKED; DRAWN; DWG. NO.; REV; SIZE; 1/2" Polycarb pipe; MATERIAL; Cell: 716.400.6114; Anaheim CA 92806; Height: 21.463; SECTION A-A; Turned shoulder on the outlet material ensures that

the solvent weld joint tolerance is controlled.
Plastics have a pretty wide tolerance band from
material suppliers and since the part needs to be
turned anyway the shoulder does not add any
appreciable production time. This also makes it
easier to control fits if the turned parts are being
produced in one shop and milled parts are
produced in another.

UNLESS OTHERWISE SPECIFIED:

PROPRIETARY AND CONFIDENTIAL

WWW.KILLSTRESSDESIGNS.COM

THE INFORMATION CONTAINED IN THIS
DRAWING IS THE SOLE PROPERTY OF
TYLER SMUTZ OF KILLSTRESS DESIGNS®.
TWO PLACE DECIMAL REPRODUCTION IN PART OR AS A WHOLE
WITHOUT THE WRITTEN PERMISSION OF
KILLSTRESS DESIGNS IS PROHIBITED.

DIMENSIONS ARE IN INCHES
TOLERANCES:
FRACTIONAL
ANGULAR: MACH

Bounding Box Dimensions

ENG APPR. BEND

Length: 25.781
Width: 21.463 | Client | 1 QUANTITY: | Q.A.

THREE PLACE DECIMAL

MFG APPR.

Contact Info
Project Oscillating Vent Outlet

without warranties, representations or conditions of any kind, either express or implied. | NEXT ASSY USED ON | FINISH

DO NOT SCALE DRAWING | | Scale: 2:1 | WEIGHT: www.killstressdesigns.com

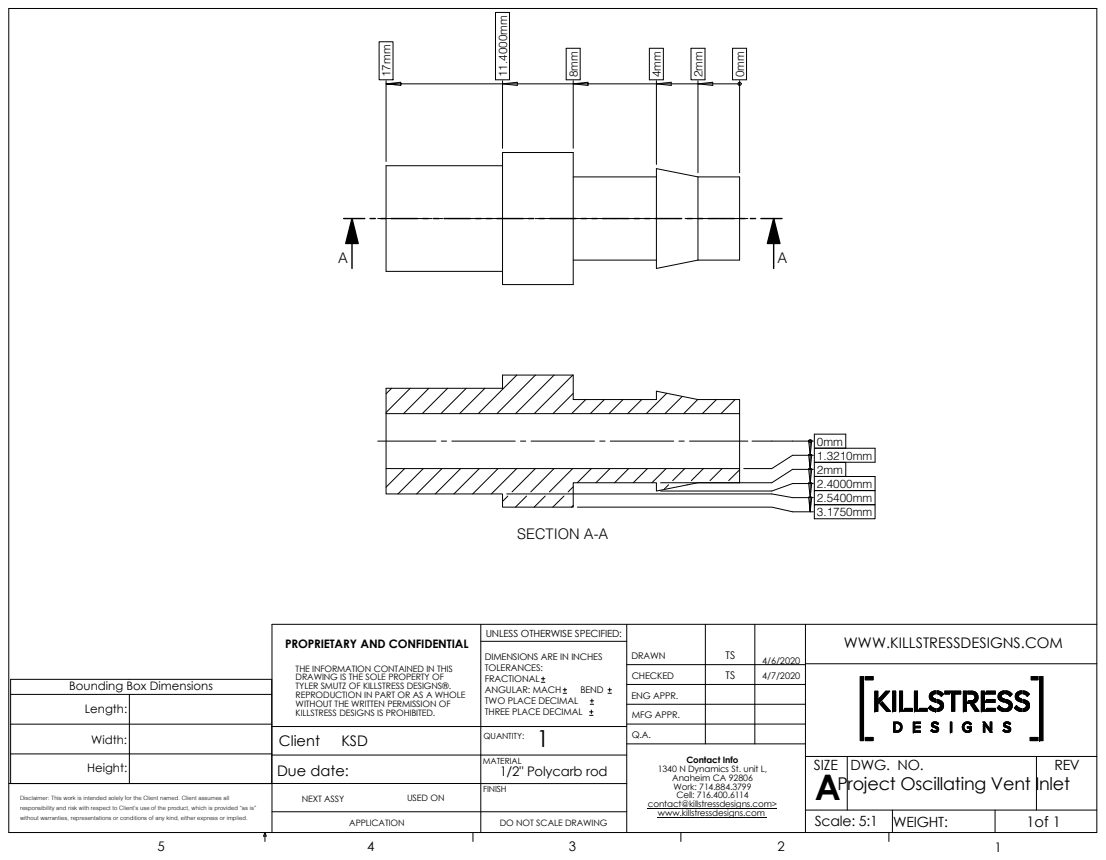
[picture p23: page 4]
DRAWN; DWG. NO.; REV; REPRODUCTION IN PART OR AS A WHOLE; TWO PLACE DECIMAL; 1/2" Polycarb rod; MATERIAL; Contact Info; Due date:; BEND; Height:; SECTION A-A

UNLESS OTHERWISE SPECIFIED:

PROPRIETARY AND CONFIDENTIAL

WWW.KILLSTRESSDESIGNS.COM

THE INFORMATION CONTAINED IN THIS
DRAWING IS THE SOLE PROPERTY OF
TYLER SMUTZ OF KILLSTRESS DESIGNS®.
WITHOUT THE WRITTEN PERMISSION OF
KILLSTRESS DESIGNS IS PROHIBITED.

DIMENSIONS ARE IN INCHES
TOLERANCES:
FRACTIONAL
ANGULAR: MACH

CHECKED | TS | 4/7/2020
ENG APPR.
MFG APPR.

Bounding Box Dimensions

Length:
Width: | | KSD Client | 1 QUANTITY: | Q.A.

THREE PLACE DECIMAL

SIZE
Project Oscillating Vent Inlet

1340 N Dynamics St. unit L,
Anaheim CA 92806
Work: 714.884.3799
Cell: 716.400.6114

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

DO NOT SCALE DRAWING | | Scale: 5:1 | 1of 1

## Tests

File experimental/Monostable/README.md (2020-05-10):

# ARMEE Monostable Design
## AKA Burns-Lunday Design

by Henry Burns (1969) and renewed with updated parameters by Jake Lunday (2020)

Note: the 3D printable models are located in "Highly Printable - Alpha I" folder.

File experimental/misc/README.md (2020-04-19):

# Miscellaneous

# Notable External Projects:

https://github.com/Cedev/fluidic-amplifiers
- Some really clever design using shaped plates bolted together to build the oscillator vertically
- also highly manufactuable and easy to assemble.  Strong project

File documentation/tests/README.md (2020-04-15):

## Tests

These are WIP and are NOT considered sufficient for validation.  Merely for pulling useful test data.

Please submit your data in Pull Requests to `/tests/<test_name>/results/<date>-<name>-<model>/` folder with whatever relevant data you'd like to submit, the model you're testing, and the context of your test described thoroughly in a Readme.txt file (we will be standardizing this more asap...)

### Enumeration Test

Estimated Test time: 50-70 minutes:

* Intended Delivered Tidal Volume:  300-500, assess every 100 ml  (simulating patients 50-83 kg, 6 ml/kg )
* Lung Compliance:  30-150, assess every 30 ml/cmH2O
* Airway Resistance: 0-15, assess every 5 cmH2O/l/sec
* Input Pressure (from Source): 50-350, every 75 cmH2O

Record the achieved PIP, PEEP, Tidal Volume, Inhale Time, Exhale Time averages over about 3 breaths or about 15 seconds. 
(feel free to increase time/breaths for greater accuracy)

Total different max combinations:  3 * 5 * 3 * 5 = 225

Total time: ~15 seconds * 225 =  56 minutes (plus setup time)

(of course, if you don't mind getting finer grained that would be amazing)

### Driving Pressure Test

Estimated Time (complete test): ~ 4 hours

Try various calibrations of PIP and PEEP set screws to get `Driving Pressure = PIP - PEEP` of 10, 15, 20, 25 cmH2O.
Trying this with each of the above enumerations...  4 * 56 minutes = about 4 hours.

This probably does not need a complete enumeration though.  We're mostly just interested in the general effect on each parameter and finding extreme values.

### PEEP Test

Try the Driving Pressure Test but with PEEP of 5, 10, 15, 20 cmH2O

(16 hours? :)  The effects on each parameter should be obvious though and should not need iterating with all combinations)

### Quality-over-time Test

(TODO: establish the over-time max (min, average) variance of parameter combinations - particularly those close to extreme values.)

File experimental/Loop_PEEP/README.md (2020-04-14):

# ARMEE PEEP Loop

This modification of the original 1965 US Army design adds a "PEEP Loop" to the right control channel, using pressure from the source air input to control switches from exhalation to inhalation, rather than atmospheric pressure.  This allows us to have positive PEEP switching pressures rather than low-to-negative switching like in the original version - which is reportedly harmful for COVID-19 patients.

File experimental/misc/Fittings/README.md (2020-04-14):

# Fittings

Small but useful print files for various fittings, reusable by multiple models

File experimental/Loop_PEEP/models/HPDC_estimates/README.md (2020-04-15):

# ARMEE PEEP-Loop HPDC Estimates

by Yannick Charron-Tousignant

These are for an aluminum-cast device, which we note is unlikely to be our chosen material for hospitals (polycarbonate or similar USP Class-6 materials are a better bet), but still gives us a good cost/speed ballpark.  Yannick would like us to point out that these estimates are rough, may need a "trim die" to remove parting line flash and gating, and is based on 1 full year worth of production - the $/part will be affected considerably depending on production volumes, mostly because of tooling costs.

Roughly, the cost would be arround $2.75/set ±1$ (lid+body) for a year's production (10M+ units). A more realistic number might be $50,000 for a die cast which can make 500,000 units (a single cast's lifetime) in about 110 days by a single machine.  Horizontal scaling would improve speed but increase total costs due to higher unit volumes paid upfront by the mold costs.

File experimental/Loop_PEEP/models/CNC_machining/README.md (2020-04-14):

# CNC-Machined ARMEE PEEP Loop

by Chris Jung

Models to implement a CNC-Milled/Machined version of the ARMEE PEEP Loop design.

Includes models for a "Test rig" with mounts for manometer etc.

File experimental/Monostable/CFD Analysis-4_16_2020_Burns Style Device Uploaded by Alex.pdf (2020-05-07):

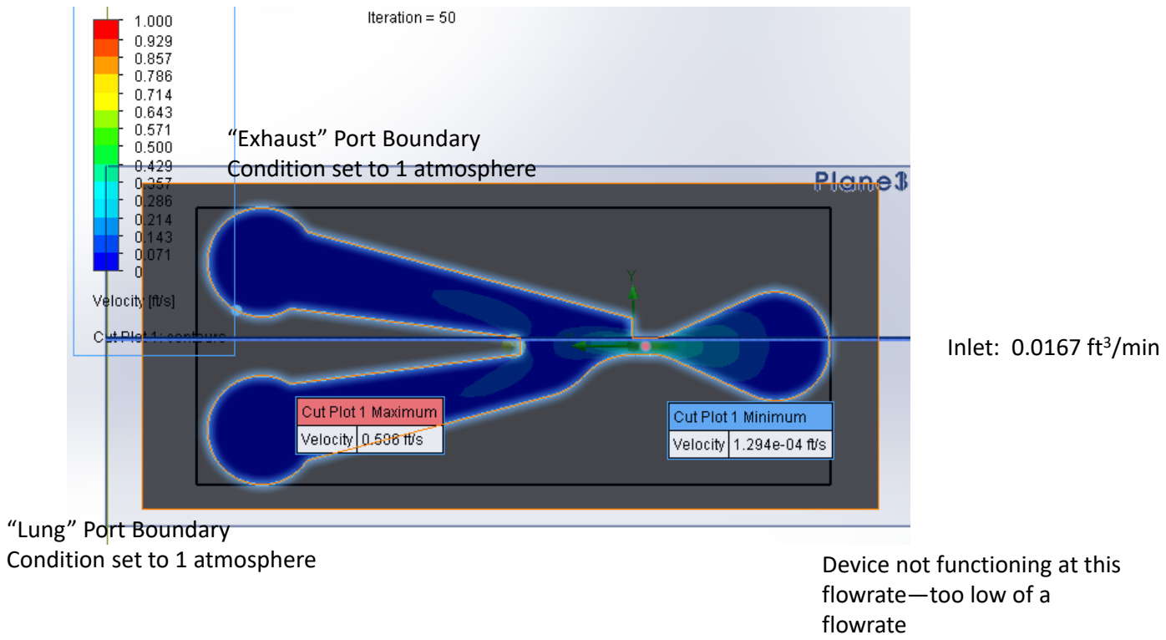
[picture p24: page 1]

Inlet: 0.0167 ft³
/min

“Lung” Port Boundary
Condition set to 1 atmosphere

“Exhaust” Port Boundary
Condition set to 1 atmosphere

Device not functioning at this flowrate—too low of a
flowrate

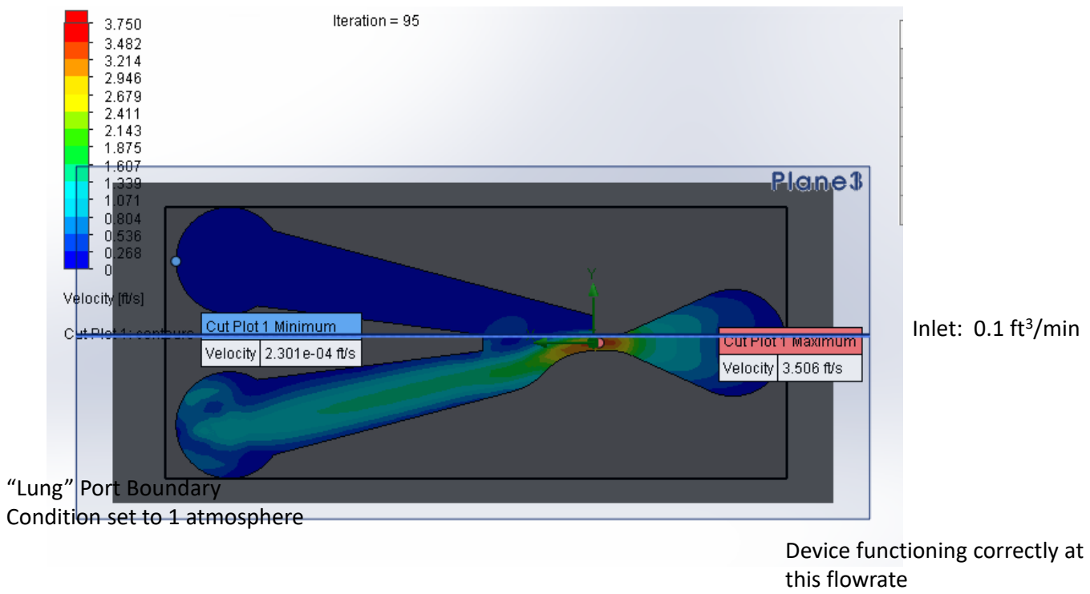
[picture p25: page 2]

Inlet: 0.1 ft³
/min

“Lung” Port Boundary
Condition set to 1 atmosphere Device functioning correctly at this flowrate

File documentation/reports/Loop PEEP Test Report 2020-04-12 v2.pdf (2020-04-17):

# Loop PEEP Test Report 2020-04-12 v2

by Alex Izvorski <aizvorski@gmail.com>

### CAD files

https://github.com/MillionVentilators/ARMEE_Ventilator_1.0/raw/master/models/Harry_Diamond_PEEP_Ry an%20v5.f3d (https://github.com/MillionVentilators/ARMEE_Ventilator_1.0/raw/master/models/Harry_Diamond_PEEP_Ryan%20v5.f3d)
https://github.com/MillionVentilators/ARMEE_Ventilator_1.0/raw/master/models/Harry_Diamond_PEEP_Ry an%20v5.step (https://github.com/MillionVentilators/ARMEE_Ventilator_1.0/raw/master/models/Harry_Diamond_PEEP_Ryan%20v5.step)

### Photos

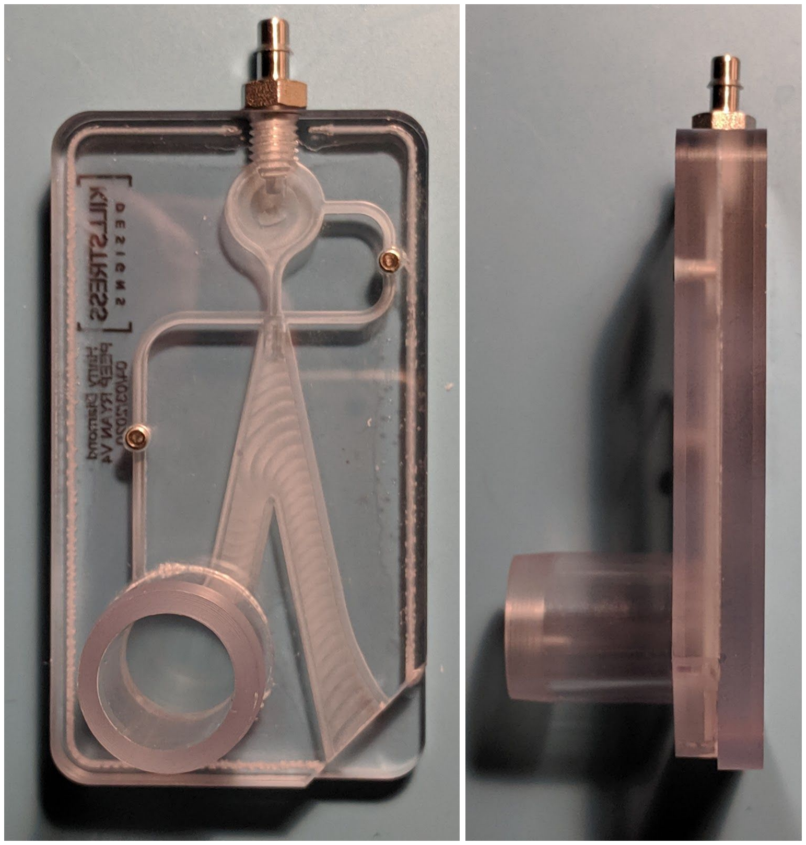
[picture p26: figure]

(as-tested device made by Tyler Smutz)

### Construction

The device is constructed from 1/4" polycarbonate sheet stock, McMaster-Carr 8574K172 (https://www.mcmaster.com/8574k172) or equivalent.

Mill the channels into the top piece to the depth and width shown in the CAD file +- 0.05mm. Channel cross section area is a critical dimension. Do NOT mill the face which will become a joint between the pieces: it should have the original smooth surface from the plastic sheet. Make sure the channel sides and bottom are smooth (surface finish ISO N6 or better).

Tap the adjustment screw holes using a M3x0.5 tap. Make sure that there are no burrs left, and the face which will be joined to the other piece is flat.

As tested: Tape the top and bottom pieces together to ensure proper alignment. Slowly inject a few ml of water-thin acrylic solvent cement, IPS Weld-On 3, SciGrip 3, McMaster-Carr 7528A13 (https://www.mcmaster.com/7528a13) or equivalent, into the "v" grooves that run around the periphery of the part. Watch the "v" grooves fill with solvent and stop filling as soon as the solvent reaches the end of the groove. Let sit for 30 minutes before removing tape. Inject the solvent using a Precision Needle-Tip Squeeze Bottle, McMaster-Carr 1902T111 (https://www.mcmaster.com/1902t111/) or equivalent, to keep the fumes contained.

(Alternate method: Spread a thin, uniform layer of solvent cement on the cover; place the piece with the channels on top of it and clamp. Best method still a work in progress)

Tap the input fitting hole using a M6x1 tap.

Adjustment screws: Stainless Steel Flat-Tip Set Screw, M3 x 0.5 mm Thread, 6 mm Long McMaster-Carr 92605A100 (https://www.mcmaster.com/92605a100)

Input fitting: Stainless Steel Barbed Tube Fitting, 4mm Tube ID, M6 x 1 mm Male McMaster-Carr 4406T772 (https://www.mcmaster.com/4406t772)

### Equipment

Ventilator analyzer: Fluke VT Plus HF (https://www.flukebiomedical.com/products/biomedical-test-equipment/gas-flow-analyzers-ventilator-testers/vt-plus-hf-gas-flow-analyzer) gas flow analyzer; can substitute Fluke VT650/VT900A, TSI Certifier FA Plus 4080, IMT Analytics Citrex H3/H4/H5 or equivalent

Air source: Porter Cable C2002; or any other oil-free compressor capable of at least 2 scfm and 50psi; or medical air wall outlet

Flow adjustment valve: McMaster-Carr 46425K12 (https://www.mcmaster.com/46425k12) or equivalent

Test lungs: rigid volume, two 5.5 gallon glass carboys, detailed construction as described in "How To Make Your Own Accurate Test Lungs for Testing Emergency Ventilators" (https://medium.com/@RobertLeeRead/how-to-make-your-own-accurate-test-lungs-for-testing-emergency-ventilators-2d68fe5ac460)

### Calibration

Connect the input of the device to a source of compressed air regulated to 50psi and with a precise flow adjustment valve at the output.

Connect the output of the device to the analyzer, and the output of the analyzer to the test lung with compliance 30 +-2 ml/cmH2O and resistance < 3 cmH2O/(liter/second).

Turn both adjustments screws so they are fully in. Do NOT overtighten as they can crack the joint between plastic pieces; just turn until they bottom out.

Close off the connection to the test lung, then open the input valve and adjust the flow to 38 +- 2 lpm.

Open the connection to the test lung.

Slowly open (turn counterclockwise) the output adjusting screw until tidal volume is 450 +- 50 ml. As this point the device should be cycling steadily, with PIP approx 25 cmH2O and PEEP at 0.

Slowly open (turn counterclockwise) the PEEP adjusting screw until PEEP is approx 10 cmH2O.

On this particular device, the output screw was open by 0.56 mm and PEEP screw by 0.14 mm.

### Results

The operation of the device is stable and cycles between PIP 25-26 cmH2O and PEEP 9-10 cmH2O. Tidal volume is 450+-20 ml.

The flow rate and airway pressure appear well behaved; see screenshots from Fluke VT Plus analyzer below.

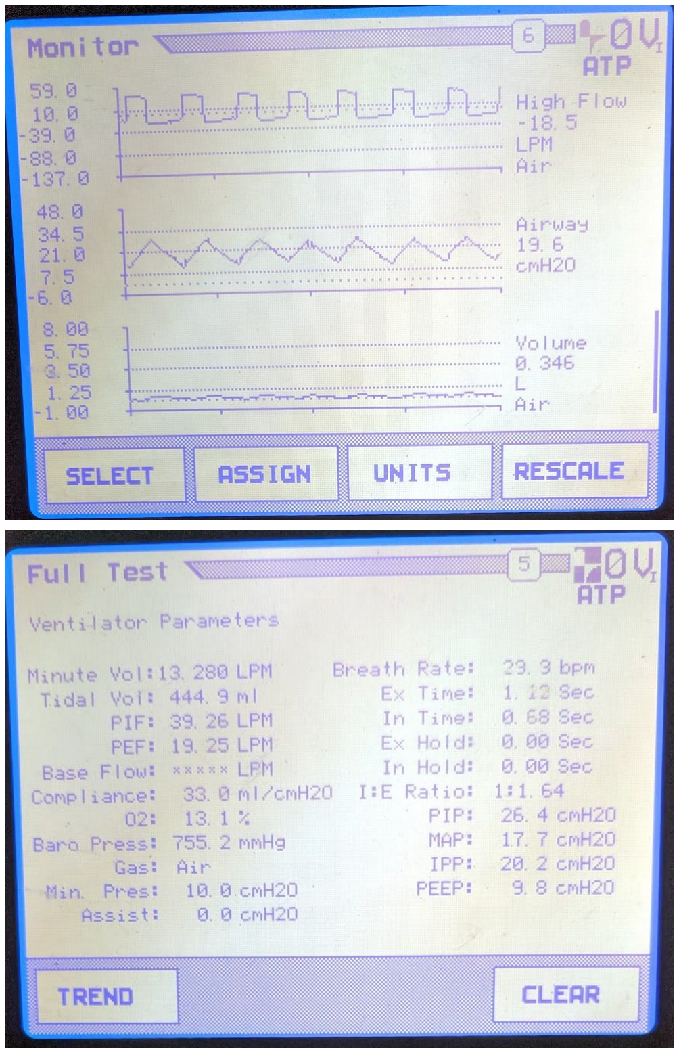
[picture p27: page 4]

However, it was not possible to get a respiratory rate significantly less than 30 bpm with this device, unless the tidal volume was also much larger.

It appears that, for a given geometry, input flow rate, and lung compliance, the rate at which airway pressure rises and falls is relatively fixed, and is not affected by the PIP/PEEP adjustments. Thus, low (or zero) PEEP results in much lower respiratory rates.

If PEEP was non-zero (adjustment screw not fully in), there is a bit of switching noise (seen as pressure fluctuations) during both transitions. This is visible in the traces above; the magnitude appears to be 3-5 cmH2O p-p. This corresponds to audible noise, probably as the flow oscillates rapidly between the two channels. Low input flow rates, and possibly some positions of the PEEP screw, can make this a lot more prominent, and it can last for much longer. This was the main reason the calibration was done at 38 lpm rather than the more typical for this design 30-34 lpm.

The operation does not appear to be affected by changes in resistance probably between R <2 and R >10.

### Further work

- Modify design to eliminate pressure fluctuations during switching
- Test effect of different lung compliance and resistance values
- For a fixed calibration, draw curves of PIP/PEEP/RR/TV versus input flow

### FAQ

Can I 3D print this?

Maybe! You're welcome to experiment (and let us know what you find).

There have been successful prints made, but we don't yet have a design we can recommend. Figuring out how to make this require less precise tolerances and a less smooth surface finish is a work in progress.

Can I mill this from materials other than polycarbonate?

Again, maybe! In general, it is the shape that matters, not the material.

A lot of our development work was done using milled aluminum pieces which were bolted together. This typically works fine. However, it is a lot harder to guarantee that the joint between the two pieces is sufficiently air-tight with metal. Also, aluminum is not recommended as a material to use in a pure oxygen atmosphere. That's why we don't recommend that style of construction outside of prototyping.

Acrylic should work equivalently to polycarbonate, but is less compatible with alcohol-based disinfectants.

Other plastics may also work, as long as the shape and tolerances can be guaranteed and the two pieces can be joined in an air-tight way. It may be possible to use another glue (not a solvent cement) or a gasket. However both may interfere with the flow channels, so we don't have a specific recommendation for a glue or gasket based build yet.

### Disclaimer

This device described here is an engineering prototype. It is not a medical device and it is not intended for use in humans. We can't guarantee absolutely anything about it, including whether it is safe, whether it is suitable for any particular use, or whether it would work the same when you build it. The specific device tested (N=1) did exactly what is described in this report. That's all.

Please see also the additional disclaimers in the CERN license.

### Copyright and license

This report is Copyright 2020 Alex Izvorski aizvorski@gmail.com

This Source (CAD files and other design materials) describes Open Hardware and is licensed under the CERN-OHL-S v2.

You may redistribute and modify this Source and make products using it under the terms of the CERN-OHL-S v2 (https:/cern.ch/cern-ohl).

This documentation is distributed WITHOUT ANY EXPRESS OR IMPLIED WARRANTY, INCLUDING OF MERCHANTABILITY, SATISFACTORY QUALITY AND FITNESS FOR A PARTICULAR PURPOSE. Please see the CERN-OHL-S v2 for applicable conditions.

Source Location: https://github.com/MillionVentilators/ARMEE_Ventilator_1.0

As per CERN-OHL-S v2 section 4, should You produce hardware based on this Source, You must maintain the Source Location visible on the external case of the hardware or other product you make using this Source.

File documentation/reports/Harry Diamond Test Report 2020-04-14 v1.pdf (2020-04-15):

# Harry Diamond (Original) Test Report 2020-04-14

v1

by Alex Izvorski <aizvorski@gmail.com>

### Calibration procedure for original

Set input flow to 22 lpm with test lungs disconnected (output venting to atmosphere) and exhaust closed

Connect test lungs - rigid construction, 11 gallons, with compliance C=28 ml/cmH2O and resistance R <2 cmH2O/(liter/second)

Set side screw fully open, set feedback screw full open

Close feedback screw until it device is cycling and PIP = 10 +- 1 cmH2O

Close side screw until TV=400 +- 50 ml

Check that PIP is still 10 +-1 cmH2O

Check that RR is 16 +-2 and I:E is around 1:2 +- 0.3

### What the screws do

Feedback screw close
PIP ++
RR -
TV -

Side screw close
TV ++
RR -
I:E - (E increases more than I) Inhale time +
Exhale time +

Vent close

Exhale time ++
RR --

Note: the vent doesn't have a screw, it can be closed partially by means of any obstruction at the outlet

### Results

Flow vs everything - flow is independent variable, the rest are the result of changing the flow

Flow | 13.6 | 15.2 | 18.3 | 19.2 | 20.3 | 22.0 | 22.7 | 24.0 | 27.6 | 30.5
MV | 3.95 | 4.65 | 5.41 | 5.98 | 6.54 | 6.73 | 6.64 | 7.11 | 8.26 | 9.2
RR | 22.6 | 22.3 | 17.7 | 18.1 | 18.5 | 16.2 | 14.9 | 14.5 | 12.6 | 12.1
TV | 175 | 208 | 305 | 330 | 354 | 415 | 446 | 491 | 656 | 760
PIF | 16.74 | 18.68 | 22.4 | 23.55 | 24.89 | 27.01 | 27.81 | 29.48 | 33.89 | 37.39
IE | 1.58 | 2.16 | 2.19 | 2.06 | 2 | 2.27 | 2.41 | 2.36 | 2.37 | 2.32
PIP | 5.6 | 6.1 | 8.3 | 9.8 | 9.2 | 9.8 | 11.2 | 12 | 16.9 | 19
PEEP | -1.6 | -2 | -3.7 | -3.4 | -3.4 | -4.8 | -5.8 | -7.1 | -9 | -9.4

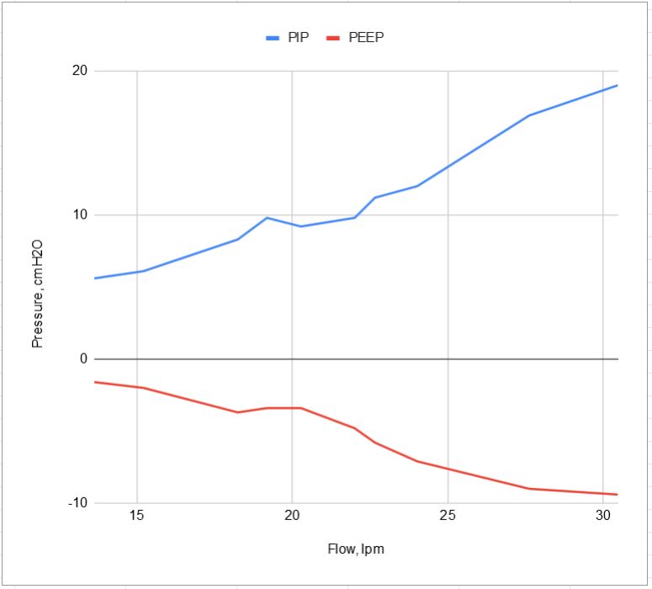
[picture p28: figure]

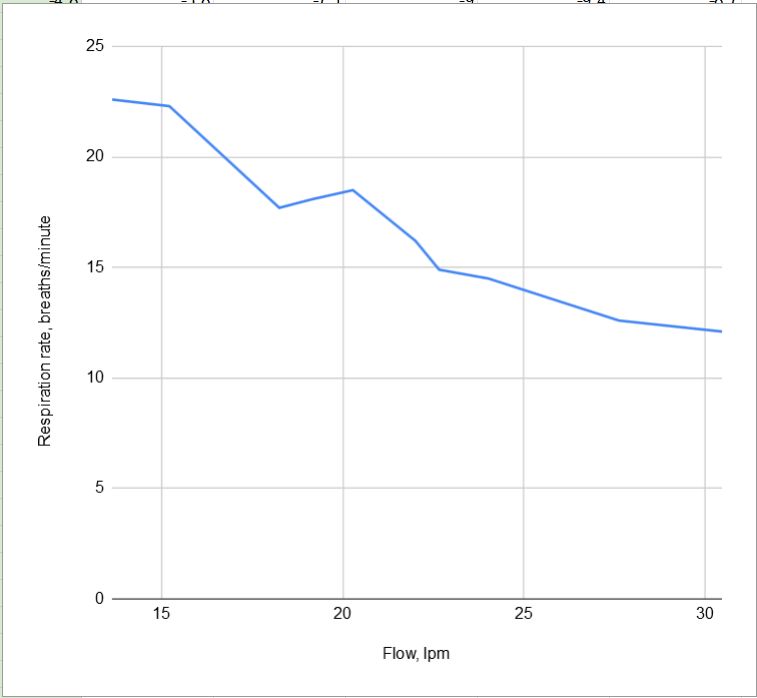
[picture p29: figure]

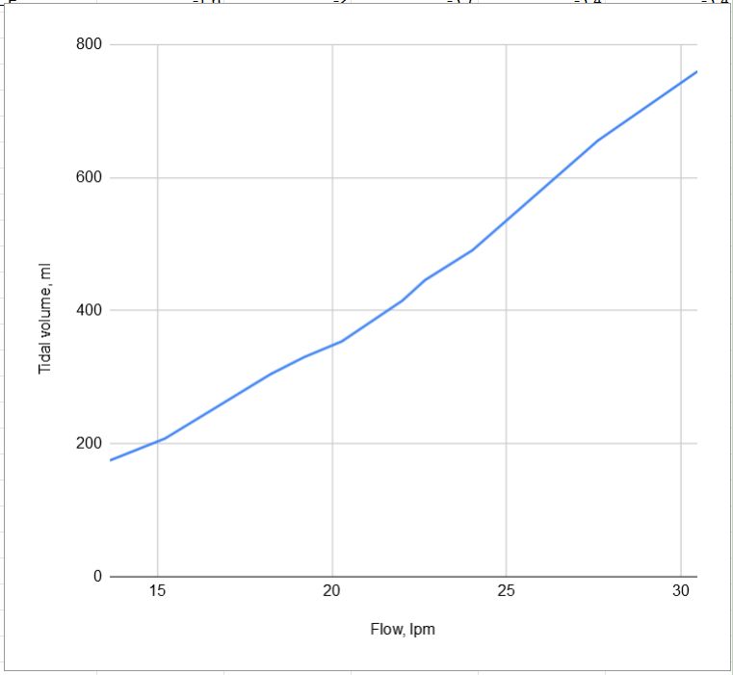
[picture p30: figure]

### Copyright and license

This report is Copyright 2020 Alex Izvorski aizvorski@gmail.com

This Source (CAD files and other design materials) describes Open Hardware and is licensed under the CERN-OHL-S v2.

You may redistribute and modify this Source and make products using it under the terms of the CERN-OHL-S v2 (https:/cern.ch/cern-ohl).

This documentation is distributed WITHOUT ANY EXPRESS OR IMPLIED WARRANTY, INCLUDING OF MERCHANTABILITY, SATISFACTORY QUALITY AND FITNESS FOR A PARTICULAR PURPOSE. Please see the CERN-OHL-S v2 for applicable conditions.

Source Location: https://github.com/MillionVentilators/ARMEE_Ventilator_1.0

As per CERN-OHL-S v2 section 4, should You produce hardware based on this Source, You must maintain the Source Location visible on the external case of the hardware or other product you make using this Source.

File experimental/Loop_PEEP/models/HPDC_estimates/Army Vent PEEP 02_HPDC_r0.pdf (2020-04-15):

clamping force | 100 | US ton | 200,000 | lbf | clamping force | 600 | US ton | 1,200,000 | lbf
intensification pressure | 10,000 | psi | intensification pressure | 10,000 | psi
maximum projected area | 20.000 | in^2 | maximum projected area | 120.000 | in^2
part projected area | 5.50000 | in^2 | part projected area | 5.50000 | in^2
runner, venting & o-f projected areas multiplicator | 1.5 | runner, venting & o-f projected areas multiplicator | 3.0
approx. runner, venting & o-f projected areas | 8.25000 | in^2 | approx. runner, venting & o-f projected areas | 16.50000 | in^2
max. cavity # | 2 | cavity | max. cavity # | 18 | cavity
approx. production rate | 4.5 | cycles/min | approx. production rate | 1.5 | cycles/min
8 | h/shift | 8 | h/shift
3 | shift/day | 3 | shift/day
365 | days/year | 365 | days/year
OEE | 70 | % | OEE | 70 | %
3.2 | set/min | 9.5 | set/min
189 | set/hour | 567 | set/hour
4,536 | set/day | 13,608 | set/day
31,752 | set/week | 95,256 | set/week
11,589,480 | set/year | 34,768,440 | set/year
material ASTM B85 A380.0, A360.0, A413 | material ASTM B85 A380.0, A360.0, A413
material price | $ | 0.7000 | $US/lb | A380.1 | material price | $ | 0.7000 | $US/lb | A380.1
part1 weight | 0.110 | lb | part1 weight | 0.110 | lb
part2 weight | 0.154 | lb | part2 weight | 0.154 | lb
die cast production | $ | 250.00 | $US/hr | die cast production | $ | 250.00 | $US/hr
approximate die cost | $ | 50,000.00 | $US | approximate die cost | $ | 250,000.00 | $US
approximate die life | 500,000 | cycles/die | approximate die life | 500,000 | cycles/die
secondary operations | 30 | s/set | secondary operations | 30 | s/set
secondary operations rate | $ | 30.00 | $US/hr | secondary operations rate | $ | 30.00 | $US/hr
Unit price | Unit price
secondary operations price | $ | 0.2500 | $/set | secondary operations price | $ | 0.2500 | $/set
die price | $ | 0.1000 | $/set | die price | $ | 0.5000 | $/set
material price | $ | 0.2772 | $/set | material price | $ | 0.5544 | $/set
die cast production price | $ | 1.3228 | $/set | die cast production price | $ | 0.4409 | $/set
subtotal $ | 1.9500 $/set | subtotal $ | 1.7453 $/set
profit margin | 45 % | profit margin | 45 %
HPDC cost/sale price $ 2.8274 $/set (ready to tap) | HPDC cost/sale price $ 2.5307 $/set (ready to tap)

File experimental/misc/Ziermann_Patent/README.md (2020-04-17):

# Ziermann Ventilator

Hermann Ziermann. ["Fluid amplifier controlled respirator"](https://patents.google.com/patent/US3379194A/en). US Patent 3,379,194, 1968

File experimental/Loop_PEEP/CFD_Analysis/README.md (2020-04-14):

[CFD Analysis](https://docs.google.com/document/d/1qQthCbZD3XL3UNKIDL2VmaANc0YivP65JDUYH6OkK6Y
) and [Geometry](
https://helpfulengineering.slack.com/files/U010BGV1F53/F010N66B4UU/geom.stp?origin_team=TUTSYURT3&origin_channel=C0108F4D0RE) by Nikhil Varma:

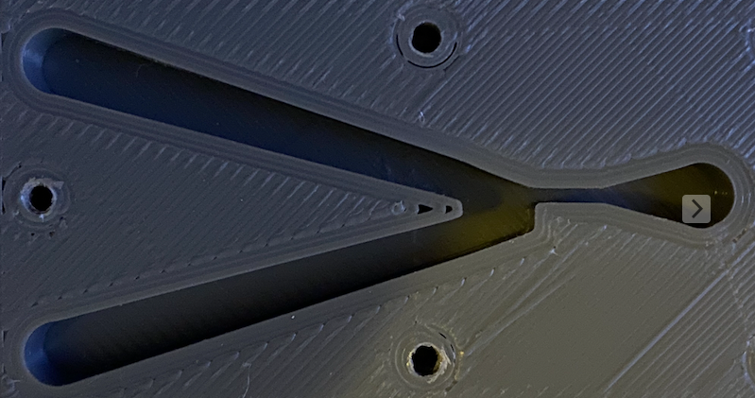
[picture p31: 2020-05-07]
experimental/Monostable/images/pic3.png

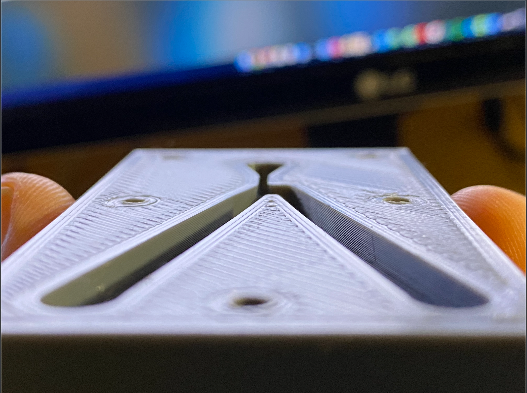
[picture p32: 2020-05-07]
experimental/Monostable/images/pic2.png

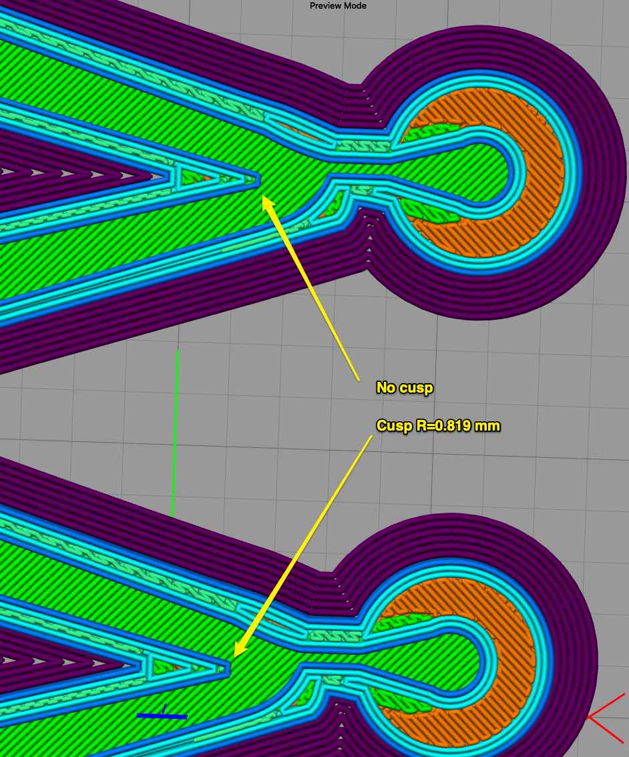
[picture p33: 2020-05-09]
experimental/Monostable/images/closeup.png

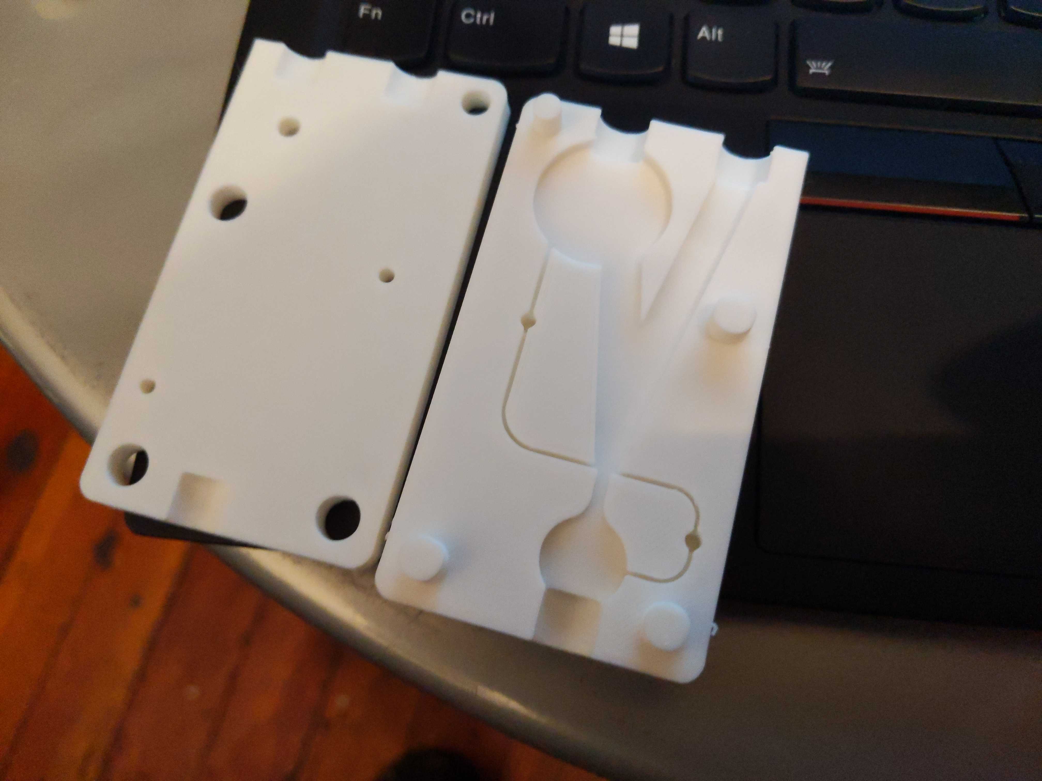
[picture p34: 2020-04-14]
experimental/Loop_PEEP/images/mendoza_3d_peep_loop.jpg

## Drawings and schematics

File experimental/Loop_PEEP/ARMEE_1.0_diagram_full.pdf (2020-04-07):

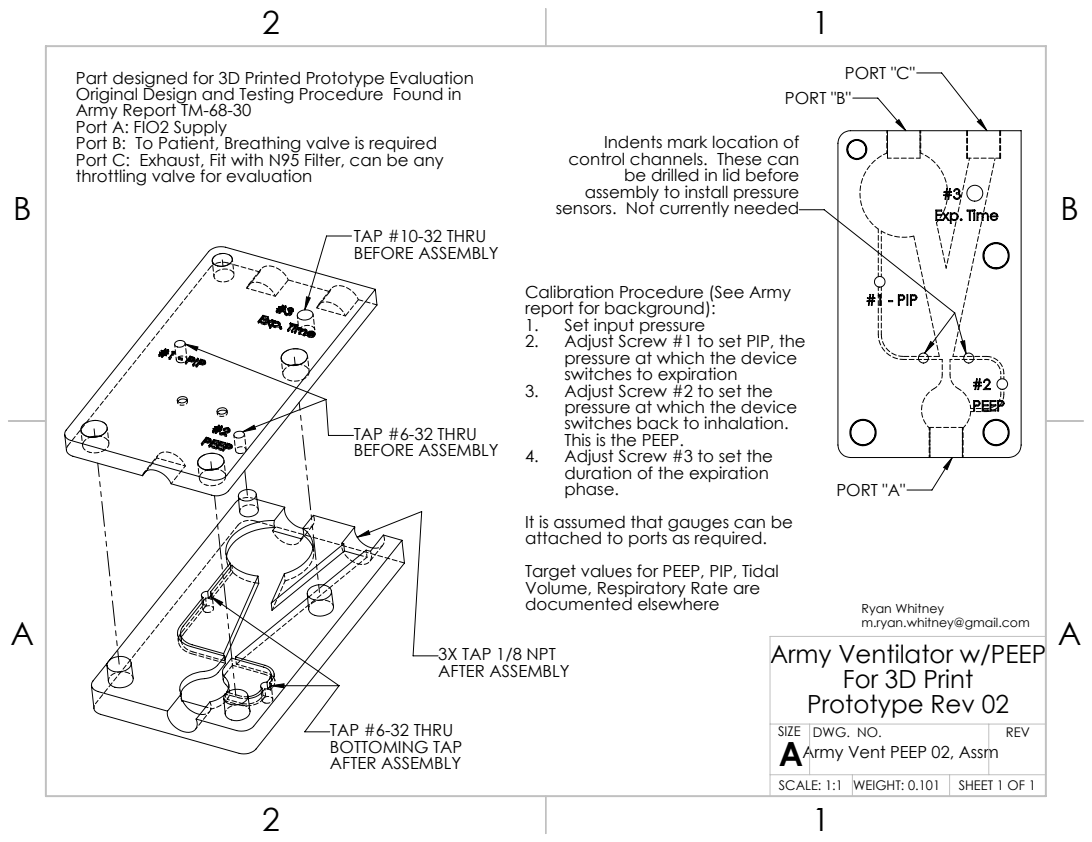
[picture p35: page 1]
PORT "B"; PORT "C"; PORT "A"; TAP #6-32 THRU BEFORE ASSEMBLY; TAP #10-32 THRU BEFORE ASSEMBLY; TAP #6-32 THRU BOTTOMING TAP AFTER ASSEMBLY; 3X TAP 1/8 NPT AFTER ASSEMBLY; documented elsewhere; Ryan Whitney

Part designed for 3D Printed Prototype Evaluation
Original Design and Testing Procedure Found in
Army Report TM-68-30
Port A: FIO2 Supply
Port B: To Patient, Breathing valve is required
Port C: Exhaust, Fit with N95 Filter, can be any
throttling valve for evaluation

Indents mark location of
control channels. These can
be drilled in lid before
assembly to install pressure
sensors. Not currently needed

Calibration Procedure (See Army
report for background):
1. Set input pressure
2. Adjust Screw #1 to set PIP, the
pressure at which the device
switches to expiration
3. Adjust Screw #2 to set the
switches back to inhalation.
This is the PEEP.
4. Adjust Screw #3 to set the
duration of the expiration
phase.
It is assumed that gauges can be
attached to ports as required.
Target values for PEEP, PIP, Tidal
Volume, Respiratory Rate are

m.ryan.whitney@gmail.com
Army Ventilator w/PEEP
For 3D Print
Prototype Rev 02

SIZE A Army Vent PEEP 02, Assm | DWG. NO. | REV

SCALE: 1:1 | WEIGHT: 0.101 | SHEET 1 OF 1

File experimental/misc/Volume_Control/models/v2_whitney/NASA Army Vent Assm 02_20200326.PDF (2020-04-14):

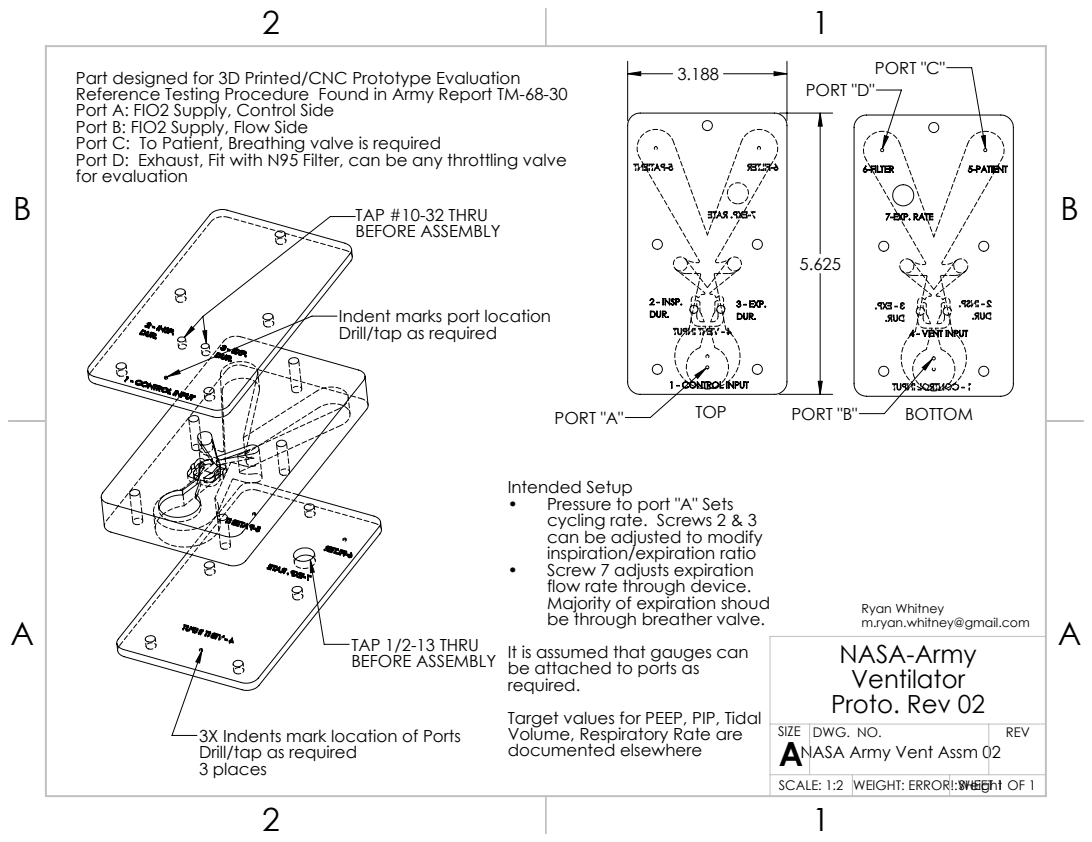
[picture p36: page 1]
PORT "A"; TOP; TAP #10-32 THRU BEFORE ASSEMBLY; TAP 1/2-13 THRU BEFORE ASSEMBLY; PORT "D"; PORT "C"; PORT "B"; BOTTOM; inspiration/expiration ratio •; Screw 7 adjusts expiration

Part designed for 3D Printed/CNC Prototype Evaluation
Reference Testing Procedure Found in Army Report TM-68-30
Port A: FIO2 Supply, Control Side
Port B: FIO2 Supply, Flow Side
Port C: To Patient, Breathing valve is required
Port D: Exhaust, Fit with N95 Filter, can be any throttling valve
for evaluation

Indent marks port location
Drill/tap as required

Intended Setup
• Pressure to port "A" Sets
cycling rate. Screws 2 & 3
can be adjusted to modify
flow rate through device.
Majority of expiration shoud
be through breather valve.
It is assumed that gauges can
be attached to ports as
required.
Target values for PEEP, PIP, Tidal
Volume, Respiratory Rate are
documented elsewhere

Ryan Whitney
m.ryan.whitney@gmail.com
NASA-Army
Ventilator
Proto. Rev 02

SIZE A NASA Army Vent Assm 02 | DWG. NO. | REV

3X Indents mark location of Ports
3 places

SCALE: 1:2 | WEIGHT: ERROR!:Weight | SHEET 1 OF 1

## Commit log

2020-04-07 Hello world
    [ARMEE_1.0_base.sldprt, ARMEE_1.0_base.stl, ARMEE_1.0_lid.sldprt, ARMEE_1.0_lid.stl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]
2020-04-10 These have 22mm ports on the lid vs. axial ports
    [Army Vent PEEP 03, Body.SLDPRT, Army Vent PEEP 03, Body_20200410.STL, Army Vent PEEP 03, Lid.sldprt, Army Vent PEEP 03, Lid_20200410.STL]
2020-04-10 Create printable
2020-04-11 First version
    [ArmyVentPEEP02 BRICK REV AMG.stl]
2020-04-11 Printable versions
    [ARMEE_1.0_3D_printabl_snap_bottom.stl, ARMEE_1.0_3D_printable_snap_bottom_with_enclosure.stl, ARMEE_1.0_3D_printable_snap_top.stl, ARMEE_1.0_printable_brick_fa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]
2020-04-13 Upload CAD files for as-tested device
    [Harry_Diamond_PEEP_Ryan v4.f3d, Harry_Diamond_PEEP_Ryan v4.step, Harry_Diamond_PEEP_Ryan v5.f3d, Harry_Diamond_PEEP_Ryan v5.step]
2020-04-14 Big restructure, including experimental designs
    [ARMEE_1.0_3D_printabl_snap_bottom.stl, ARMEE_1.0_3D_printable_snap_bottom_with_enclosure.stl, ARMEE_1.0_3D_printable_snap_top.stl, ARMEE_1.0_base.sldprt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]
2020-04-14 Rename default models to reference_design
    [ARMEE_1.0_3D_printabl_snap_bottom.stl, ARMEE_1.0_3D_printable_snap_bottom_with_enclosure.stl, ARMEE_1.0_3D_printable_snap_top.stl, ARMEE_1.0_base.sldprt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]
2020-04-15 Moved to documentation. Added HPDC estimates
    [Army Vent PEEP 02, Body_HPDC_r0.STEP, Army Vent PEEP 02, Lid_HPDC_r0.STEP]
2020-04-16 Add files via upload
    Print these two pieces successfully BEFORE trying to print a unibody Armee version to test your printer capabilities. If you cannot print them with the roof of the bottom channel, then you need to ca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
    [Bridge Test 1.stl, Bridge Test 2.stl]
2020-04-16 Big reorg to flatten directory tree: models/experimental/ -> experimental/, models/stable/ARMEE_1.0/ -> models/ and some more
    [ARMEE_1.0_3D_printabl_snap_bottom.stl, ARMEE_1.0_3D_printable_snap_bottom_with_enclosure.stl, ARMEE_1.0_3D_printable_snap_top.stl, ARMEE_1.0_base.sldprt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]
2020-04-17 Valve PEEP - side port and exhaust port connected together
    [Valve_PEEP v2.f3d, Valve_PEEP v2.step, Valve_PEEP v5.f3d, Valve_PEEP v5.step]
2020-04-20 New version - based on DFM
    [Valve_PEEP v7.f3d, Valve_PEEP v7.step]
2020-04-20 New model - original version modified for easier manufacturing; all connectors at right angles
    [Harry_Diamond_DFM v4.f3d, Harry_Diamond_DFM v4.step]
2020-04-20 Loop PEEP with 3-way adjustment and connetor for external buffer
    [Loop_PEEP_3Way v3.f3d, Loop_PEEP_3Way v3.step]
2020-04-20 Remove old/obsolete valve peep models, use v7 or later
    [Valve_PEEP v2.f3d, Valve_PEEP v2.step, Valve_PEEP v5.f3d, Valve_PEEP v5.step]
2020-04-21 Rename Valve_PEEP to Exhaust_PEEP to avoid confusion with (patient) valve
    [Exhaust_PEEP v7.f3d, Exhaust_PEEP v7.step, Valve_PEEP v7.step]
2020-05-07 Added circuit diagram
2020-05-07 Renamed models to stable
    [Harry_Diamond_Respirator_v9.f3d, Harry_Diamond_Respirator_v9.step]
2020-05-09 Uploaded files of the Monostable Design
    Here's the files from the test monostable files---modified version of the Henry Burns design.
    [Assembly_Monostable Fluidic Amplifier_Alpha Design_Nozzle_1.3mm__Radius_63.5mm__Channel Depth_6mm__Fillet_0mm.SLDPRT, Assembly_Monostable Fluidic Amplifier_Alp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]
2020-05-09 Moved Jake's Monostable model to folder
    [Assembly_Monostable Fluidic Amplifier_Alpha Design_Nozzle_1.3mm__Radius_63.5mm__Channel Depth_6mm__Fillet_0mm.SLDPRT, Assembly_Monostable Fluidic Amplifier_Alp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]
2020-05-10 Public Release - Alpha I - Highly Printable
    [Alpha I Rev1 - Actuator.stl, Alpha I Rev1 - Patch for FDM Unibody.stl, Alpha I Rev1 - Top.stl, Alpha I Rev1 - Unibody FDM.stl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]
2020-05-10 AMG first Version
    [Alpha I Rev1 - Actuator.stl, Alpha I Rev1 - Patch for FDM Unibody.stl, Alpha I Rev1 - Top.stl, Alpha I Rev1 - Unibody FDM.stl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]
2020-05-10 Removed highly-printable alpha 1 from root
    [Alpha I Rev1 - Actuator.stl, Alpha I Rev1 - Patch for FDM Unibody.stl, Alpha I Rev1 - Top.stl, Alpha I Rev1 - Unibody FDM.stl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]
2020-05-13 Small version
    [Alpha | Rev1 - Patch for FDM Unibody - small.stl]
2020-05-13 Rig for testing patch fitness
    Use this piece for testing if the Patch will fit your print
    [Alpha I Rev1 - Testing Gasket.stl]
